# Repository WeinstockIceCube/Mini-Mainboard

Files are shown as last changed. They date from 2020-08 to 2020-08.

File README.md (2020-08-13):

# Mini-Mainboard

This is the public repository for the Altium Project of the Mini-Mainboard for the IceCube calibration devices. 

Further detailed information on the Mini-Mainboard can be found in the DSN on Sharepoint:
https://uwprod.sharepoint.com/:p:/r/sites/icecubeupgrade/_layouts/15/Doc.aspx?sourcedoc=%7Bfcc1f85e-5ff4-41bf-9258-8532a31561ea%7D&action=edit&uid=%7BFCC1F85E-5FF4-41BF-9258-8532A31561EA%7D&ListItemId=355&ListId=%7B73D152DA-70C4-4B92-ADC9-80C59B2FEBA2%7D&odsp=1&env=prod

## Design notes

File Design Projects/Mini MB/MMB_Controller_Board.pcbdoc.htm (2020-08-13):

Reporting Options

# File in Newer Format

Date | : | 12.08.2020
Time | : | 15:29:28
Filename | : | Y:\My Hardware\Altium\IceCube\Mini-Mainboard\MMB_Controller (2-27-2020 2-48-15 PM)\Design Projects\Mini MB\MMB_Controller_Board.pcbdoc

Version | Warning
Release 20.0 | CAUTION - Support of propagation delay for primitives

This file was generated by a later version of the software

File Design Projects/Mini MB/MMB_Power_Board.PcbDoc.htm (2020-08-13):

Reporting Options

# File in Previous Format

Date | : | 13.08.2020
Time | : | 14:24:16
Filename | : | Y:\My Hardware\Altium\IceCube\Mini-Mainboard\MMB_Controller (2-27-2020 2-48-15 PM)\Design Projects\Mini MB\MMB_Power_Board.PcbDoc

Version | Warning

This file was generated by an earlier version of the software

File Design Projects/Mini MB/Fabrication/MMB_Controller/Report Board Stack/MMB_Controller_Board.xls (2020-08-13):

Board Stack Report
Stack Up |  | Layer Stack
Layer | Board Layer Stack | Name | Material | Thickness | Constant
1 |  | Top Paste
2 |  | Top Silk
3 |  | Top Mask | Solder Mask | 0,40mil | 3,5
4 |  | Layer 1 | Copper | 0,70mil
5 |  | Dielectric 1 | 370HR or Equiv | 5,00mil | 4
6 |  | Layer 2P | Copper | 0,70mil
7 |  | Dielectric 2 | 370HR or Equiv | 6,00mil | 4
8 |  | Layer 3 | Copper | 0,71mil
9 |  | Dielectric 3 | 370HR or Equiv | 6,00mil | 4
10 |  | Layer 4 Pow | Copper | 1,38mil
11 |  | Dielectric 4 | 370HR or Equiv | 26,00mil | 4
12 |  | Layer 5 | Copper | 1,38mil
13 |  | Dielectric 5 | 370HR or Equiv | 6,00mil | 4
14 |  | Layer 6 | Copper | 0,71mil
15 |  | Dielectric 6 | 370HR or Equiv | 6,00mil | 4
16 |  | Layer 7P | Copper | 0,70mil
17 |  | Dielectric 7 | 370HR or Equiv | 5,00mil | 4
18 |  | Layer 8 | Copper | 0,70mil
19 |  | Bottom Mask | Solder Mask | 0,40mil | 3,5
20 |  | Bottom Silk
21 |  | Bottom Paste
 | Height : 67,77mil

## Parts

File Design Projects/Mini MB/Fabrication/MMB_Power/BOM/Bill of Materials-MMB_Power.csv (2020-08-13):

Designator | DesignItemId | Quantity | LibRef | Footprint | Manufacturer | Manufacturer Part Number | Supplier 1 | Supplier Part Number 1 | Supplier Stock 1 | Supplier Unit Price 1
C14, C15, C16, C17, C18, C19, C20, C21, C23, C24, C25, C26, C37, C38 | CapC_470nF_1812_450V | 14 | CapC_470nF_1812_450V | 1812 | TDK | CGA8N4X7T2W474M230KE | Digi-Key | 445-7993-1-ND
C22, C29, C39 | CapC_1000pF_1206_1000V | 3 | CapC_1000pF_1206_1000V | CAPC_1206 | KEMET | C1206X102KDRACAUTO | Digi-Key | 399-16729-1-ND
C27, C28 | CAP_FILM_10UF_250V_RAD | 2 | CAP_FILM_10UF_250V_RAD | Cap Radial 1.24" x 0.492" x 0.846 | EPCOS Inc | B32524R3106K | Digi-Key | 495-4799-ND
C30 | CapC_0.1uF_603_50V_GCJ | 1 | CapC_0.1uF_603_50V_GCJ | CAPC_0603 | Murata | GCJ188R71H104KA12D | Digi-Key | 490-5798-1-ND
C31, C32, C33, C34, C35, C36 | CapC_10uF_1206_16V | 6 | CapC_10uF_1206_16V | CAPC_1206 | Murata | GCJ31CR71C106KA15L | Digi-Key | 490-10558-1-ND
D1 | DIODE AVALANCHE 200V 2.0A | 1 | DIODE AVALANCHE 200V 2.0A | DO-214AC | Vishay Semiconductors | BYG22DHE3_A/H | Digi-Key | BYG22DHE3_A/HGICT-ND
L1, L8 | INDUCTOR COM MODE FERR 470.0UH SMD | 2 | INDUCTOR COM MODE FERR 470.0UH SMD | CM6350 | API Delevan Inc | CM6350R-474 | Digi-Key | DN42155-ND
L2, L3, L4, L7, L9, L12 | Ferrite BLM31KN471SH1L | 6 | Ferrite BLM31KN471SH1L | IND_1206 | Murata | BLM31KN471SH1L | Digi-Key | 490-16529-1-ND
L5, L6, L10, L11 | Inductor_330uH_590mA | 4 | Inductor_330uH_590mA | IND_SMD_2P_10.4x10.4x4.8H | TDK EPCOS | B82464G4334M000 | Digi-Key | 495-1804-1-ND
M1 | DC-DC 24 Pin 5Vo | 1 | DC-DC 24 Pin 5Vo | DC_DC_24DIP_9P__V1 | Traco Power | TEN8-7211WI | Digi-Key | 1951-2576-ND
P7 | Header Male SL-5-VERT | 1 | Header Male SL-5-VERT | Header Male 5 Vert | Molex | 70543-0109 | Digi-Key | WM4125-ND
PAB | 61201020621 | 1 | 61201020621 | 61201020621
PTP1 | Test Point SM | 1 | Test Point SM | Test Point SM | Keystone Electronics | 5019 | Digi-Key | 5019KCT-ND
PX3 | Harwin 4x1 2mm | 1 | Harwin 4x1 2mm | HARWIN M80-8820442 | Harwin | M80-8820442 | Digi-Key | 952-1071-5-ND
PX4 | Harwin 5x1 2mm | 1 | Harwin 5x1 2mm | HARWIN M80-8820542 | Harwin | M80-8820542 | Digi-Key | 952-1072-5-ND
R17, R18, R19, R20 | R_4.7M_1206_1% | 4 | R_4.7M_1206_1% | RES_1206 | Rohm | KTR18EZPF4704 | Digi-Key | RHM4.7MAICT-ND
RX10 | R_ZERO_805 | 1 | R_ZERO_805 | RES_0805 | Panasonic | ERJ6GEY0R00V | Digi-Key | P0.0ACT-ND
SC1, SC2 | Spring Contact | 2 | Spring Contact | Spring Contact SM | Harwin | S1941-42R | Digi-Key | 952-3245-1-ND
WT1, WT2, WT3, WT4, WT5, WT6, WT7 | Test Point Turret | 7 | Test Point Turret | Turret-1592 | Mill-Max | 2506-3-00-80-00-00-07-0 | Digi-Key | ED11398-ND

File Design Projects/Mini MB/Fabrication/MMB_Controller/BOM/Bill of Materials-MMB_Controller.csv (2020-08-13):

Designator | DesignItemId | Quantity | Footprint | Manufacturer | Manufacturer Part Number | Supplier 1 | Supplier Part Number 1
C1, C2, C3, C4, C40, C43, C45, C46, C47, C50, C55, C56, C57, C58, C59, C60, C61, C62, C63, C64, C65, C66, C67, C96, C98, C100, C102, C104, C105, C106, C108, C131, C132 | CapC_0.1uF_603_50V | 33 | CAPC_0603 | TDK | CGJ3E2X7R1H104K080AA | Digi-Key | 445-8122-1-ND
C5, C8, C11, C51, C54, C68, C70, C72, C73, C74, C75, C77, C79, C80, C81, C82, C84, C86, C87, C88, C89, C91, C93, C94, C95, C110, C115, C119, C123, C133, C134 | CapC_10uF_805_10V | 31 | CAPC_0805 | Murata | GCJ21BR71A106KE01L | Digi-Key | 490-12646-1-ND
C6, C7, C9, C10, C12, C13, C41, C49, C69, C71, C76, C78, C83, C85, C90, C92, C116, C117, C118, C120, C121, C122, C124, C125, C126 | CapC_0.1uF_603_50V_GCJ | 25 | CAPC_0603 | Murata | GCJ188R71H104KA12D | Digi-Key | 490-5798-1-ND
C42 | CapC_10uF_1206_16V | 1 | CAPC_1206 | Murata | GCJ31CR71C106KA15L | Digi-Key | 490-10558-1-ND
C44, C48 | CMP-2000-06338-1 | 2 | CAPC1608X90X35LL10T15 | Murata
C52, C53 | CapC_2.2uF_805_16V | 2 | CAPC_0805 | Murata | GCJ21BR71C225KA13L | Digi-Key | 490-5801-1-ND
C97, C99, C101, C103, C107, C109, C111, C114, C127, C129 | CapC_1.0uF_603_25V | 10 | CAPC_0603 | Murata | GCJ188R71E105KA01D | Digi-Key | 490-14409-1-ND
C112, C113, C128, C130 | CapC_1000pF_603_50V | 4 | CAPC_0603 | Knowles Syfer | 0603Y0500102KXT | Digi-Key | 1608-1367-1-ND
D2, D3 | Diode ESD Pair | 2 | SOT-23 | ON Semiconductor | SBAT54SLT1G | Digi-Key | SBAT54SLT1GOSCT-ND
ICM1 | Ice Comms Module | 1 | Ice Comms Module
ICM-J1, ICM-J2 | SFM-115-X2-XXX-D-A | 2 | SFM-115-X2-XXX-D-A | Samtec | SFM-115-02-S-D-A-K-TR | Digi-Key | SAM13245CT-ND
ICM-MH1, ICM-MH2 | Keystone 4883 | 2 | Keystone 4883 solder | Keystone Electronics | 4883 | Digi-Key | 36-4883CT-ND
J2, J3 | SMA-Vertical | 2 | SMA Vertical 200LS | Emerson Network Power Connectivity Johnson | 142-0701-231 | Digi-Key | J608-ND
L13, L14, L15, L16, L17, L18, L19, L20, L21, L22, L23, L24 | Bead SM_805_4.0A_TDK | 12 | SMD-0805 | TDK | MPZ2012S101ATD25 | Digi-Key | 445-172903-1-ND
L27, L28 | Bead SM_805_2.5A_TDK | 2 | SMD-0805 | TDK | MPZ2012S331ATD25 | Digi-Key | 445-172907-1-ND
P1, P13, P14 | 62100821021 | 3 | 62100821021
P2, P6 | 62101021021 | 2 | 62101021021
P9 | Header Male SL-6-VERT | 1 | Header Male 6 Vert | Molex | 0705430110 | Digi-Key | WM4126-ND
P10 | 61000618221 | 1 | 61000618221
P11, P12, P15 | Header Male 3M-452 15x2 | 3 | 45230-220230 | 3M | 45230-220230 | Digi-Key | 3M15579CT-ND
P16, P17 | 62100421021 | 2 | 62100421021
P33 | 62130621021 | 1 | 62130621021
PBA | 61201020621 | 1 | 61201020621
R1, R3, R4, R6 | R_243_603_1% | 4 | RES_0603 | Panasonic | ERJ3EKF2430V | Digi-Key | P243HCT-ND
R2, R5, R7, R8 | R_4.99K_603_1% | 4 | RES_0603 | Panasonic | ERJ3EKF4991V | Digi-Key | P4.99KHCT-ND
R11, R12, R13, R14, R15, R16, R25, R26, R40, R41, R42, R44, R45, R46, R47, R48, R49, R50, R51, R52, R53, R54, R55, R56, R57, R58, R59, R60, R61, R62, R63, R64, R65, R66, R67, R68, R69, R70, R71, R72 | R_28.0_603_1% | 40 | RES_0603 | Panasonic | ERJ3EKF28R0V | Digi-Key | P28.0HCT-ND
R21, R22, R23, R24 | R_3.00K_603_1% | 4 | RES_0603 | Panasonic | ERJ3EKF3001V | Digi-Key | P3.00KHCT-ND
R27, R28, R29, R30 | R_100K_603_1% | 4 | RES_0603 | Panasonic | ERJ3EKF1003V | Digi-Key | P100KHTR-ND
R31 | R_10.0K_603_1% | 1 | RES_0603 | Panasonic | ERJ3EKF1002V | Digi-Key | P10.0KHCT-ND
R33, R34, R35, R36 | R_39.2_603_1% | 4 | RES_0603 | Panasonic | ERJ-3EKF39R2V | Digi-Key | P39.2HCT-ND
R37, R38, R301, R302 | R_2.00K_603_1% | 4 | RES_0603 | Panasonic | ERJ3EKF2001V | Digi-Key | P2.00KHCT-ND
R39, R43 | R_49.9_1206_1% | 2 | RES_1206 | Panasonic | ERJ8ENF49R9V | Digi-Key | P49.9FCT-ND
R73, R74, R75, R76, R77, R78, R79, R80 | R_49.9_603_1% | 8 | RES_0603 | Panasonic | ERJ3EKF49R9V | Digi-Key | P49.9HCT-ND
TP1, TP2, TP3, TP4, TP5 | Test Point SM | 5 | Test Point SM | Keystone Electronics | 5019 | Digi-Key | 5019KCT-ND
U1, U2, U7, U17 | SN74LVC2T45QDCURQ1 | 4 | TI-DGK8_N | Texas Instruments | SN74LVC2T45MDCTTEP | Digi-Key | 296-23952-1-ND
U3 | DS24B33S+T&R | 1 | W8+2_M | Maxim | DS24B33S+T&R | Digi-Key | DS24B33S+T&RCT-ND
U4 | S25FS512SAGMFV010 | 1 | MICT-SF-16_N | Cypress | S25FS512SAGMFV010 | Digi-Key | S25FS512SAGMFV010-ND
U5 | STM32H743ZIT6 | 1 | STM-LQFP144_N | STMicroelectronics | STM32H743ZIT6 | Digi-Key | 497-17721-ND
U6, U9, U13, U15, U16 | DS90LV012ATMF | 5 | MF05A_N | TI National Semiconductor | DS90LV012ATMF/NOPB | Digi-Key | DS90LV012ATMF/NOPBCT-ND
U8 | NUP4301MR6T1G | 1 | ONSC-SC-74-6-318F-05_V | ON Semiconductor | NUP4301MR6T1G | Digi-Key | NUP4301MR6T1GOSCT-ND
U10 | LPS22HDTR | 1 | HLGA-10L | STMicroelectronics | LPS22HDTR | Digi-Key | 497-17587-1-ND
U11 | LIS3MDLTR | 1 | VFLGA-12 | STMicroelectronics | LIS3MDLTR | Digi-Key | 497-13892-1-ND
U12 | ADXL355BEZ-RL7 | 1 | E-14-1 | Analog Devices | ADXL355BEZ-RL7 | Digi-Key | ADXL355BEZ-RL7CT-ND
U14 | DS90LV011ATMF | 1 | MF05A_N | Texas Instruments | DS90LV011ATMF/NOPB | Digi-Key | DS90LV011ATMF/NOPBCT-ND

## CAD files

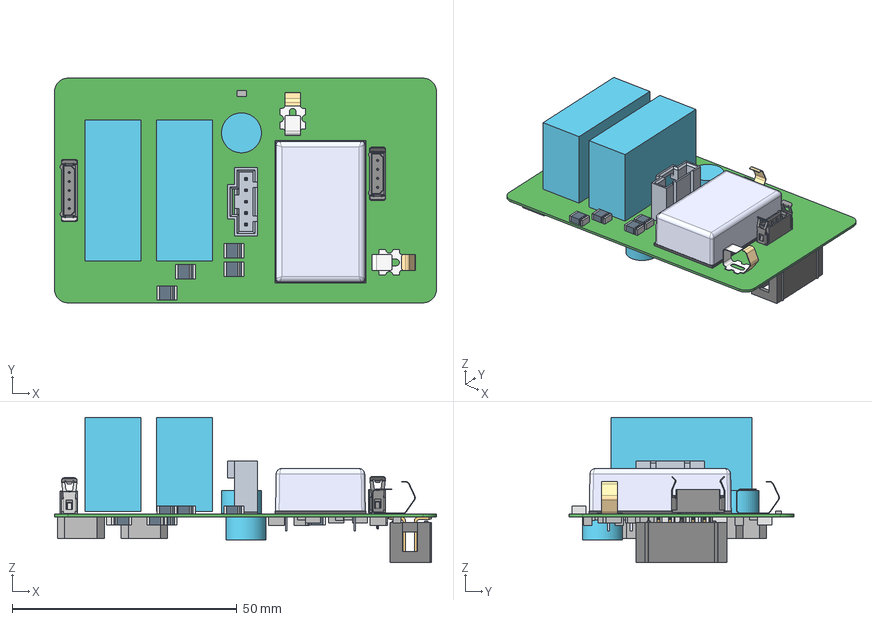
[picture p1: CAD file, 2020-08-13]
Design Projects/Mini MB/ReviewDocs/ExportSTEP/MMB_Power_Board.step
85.0 x 50.0 x 32.3 mm
s1941-42 x 2
Extruded x 99
6120xx20621_PIN x 10
M80-1000598
M80-0200049 x 9
M80-001XXXX x 4
M80-1000498
ten8wi

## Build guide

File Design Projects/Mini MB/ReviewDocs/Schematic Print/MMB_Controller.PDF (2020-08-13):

D | D
C | C
B | B
A | A

## Revisions.SchDoc

13.05.2020 | 15:40:26
Y:\My Hardware\Altium\IceCube\Mini-Mainboard\MMB_Controller (2-27-2020 2-48-15 PM)\Design Projects\Mini MB\Revisions.SchDoc
Size: | Designed:

Modified:
File:

Revision:

Time: | Sheet | of
B | Drafted: | PWS PWS
| Checked:

Started:

Approve:

# IceCube Upgrade Mini MB Schematic Revision History:

Rev1 Jan 28 2019 | Rev1.0 Prototype run of (x) PCB Assemblies SN1-SNx

# Mini MB Production History

Older Revision Perry
1. Transferred selected design files from PDOM project
2. MCU: Removed Net OSC_MCU_CLOCK from MCU Pin 8 = PC14-OSC32_IN.
3. MCU: Added Test point to OSC_MCU_OUT.
4. ICM: Added ICM_+1V8 net to J1-12. (fixed initial error with connection to J1-8)
5. ICM, XTIO: Changed LVDS signals ICM_CAL_TRIG and ICM_CAL_TIME from 3.3V psuedo-diff to 1.8V Diff SSTL 1 (0.9Vcm).
6. ALL: Re-annotated all sheets.
7. MCU: Removed redundant write-protect bypass jumper.
8. XTIO: Added SMA TRIG OUT and SMA TIME IN connectors, Diff-SE converters and jumper selects.
9. ICM: Added bypass caps on ICM Power in and out
10. MCU: Added connector for Ethernet PHY
11. MCU Changed Ethernet Connector to 2x8 x 0.1"
12. XTIO: Added jumpers for optional termination of LVDS lines
13. XTIO: Fixed net going to Pin2 of P18 to be "ICM_FPGA_CLOCK_N" (was _P)
14. MCU: Changed connector for Ethernet PHY Card to type: SFM-115-X2-XXX-D-A
15. PHY: Removed, LVS1: Removed J1, ICM: Removed USB1 and ICM-JTAG Feldhäuser:
16. ICM: P1 changed to smaller type
17. ICM: Connect Mini MB B to Mini MB A with PBA, PAB for cable connection
18. ICM: P2 changed to smaller type
19. ICM: P6 changed to smaller type
20. ICM: Connection ICM_FPGA_GPIO_0 to GND cut (R11)
21. ICM: Penetrator from ICM to LVS1 on Mini MB A
22. MCU: P10 changed to smaller type
23 XTIO P13,. P14, P16, P17 changed to smaller type
24. Delete following (only one pin, Electr. Rule Check)
: +5V0_EXT P2-4, ICM_TCK ICM-J1-18, ICM_TDI ICM-J1-14, ICM_TDO ICM-J1-16, ICM_TMS ICM-J1-20 MCU_INTLK U5-46, Aux_P3V3_EN U5-112,
MCU_CAL_A3 U5-47, MCU_GPIO_0 U5-98, MCU_GPIO_01 U5-99, MCU_GPIO_2 U5-113, NetP9_6 P9-6, NetU8_1 U8-1, NetU8_3 U8-3,
NetU12_12 U12-12, NetU12_13 U12-13, NetU12_14 U12-14
25. Delete Floating Net Label MCU_GPIO_3
26. Layer changed in PCB

# Download .pdf for component details Click on schematic symbols for component data

Temprary list made by Perry on 2-27/2-28
MCU: Added Jumpers ID0-ID3 see "DOM_Type_ID_Jumpers" in shared docs LVS1: Layout note: keep PX3 and PX4 close to each other (from same cable) LVS1: Added (2) spring contacts for grounding DC-DC converter case.
SLO: Removed L25, L26,L27,L29 Added 2x10uF bypass on magnetormeter U11 ICM: Probably need some ICM JTAG connection?
SLO: Replaced Pressure sensor with different part# for better availability

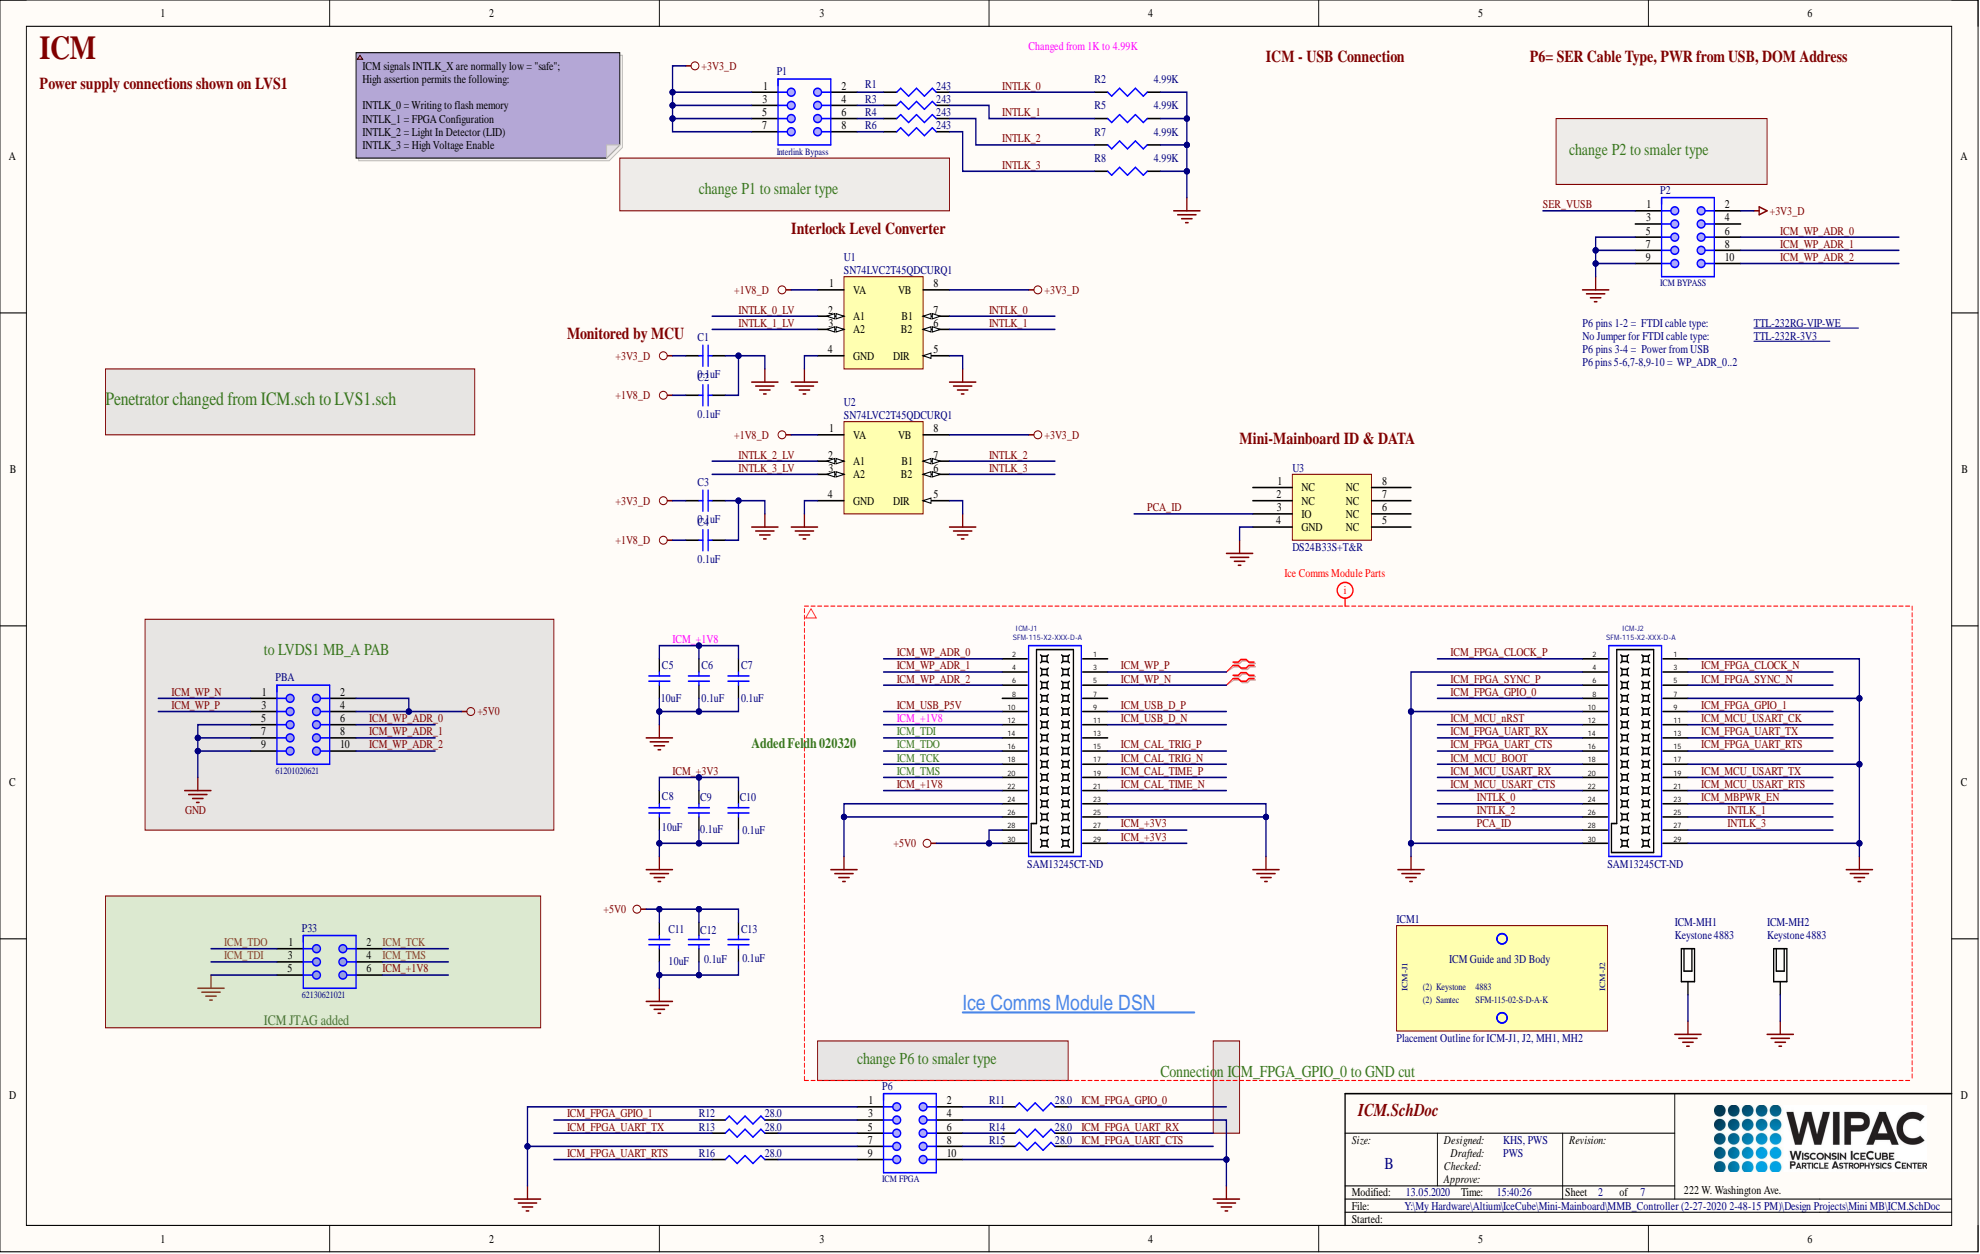
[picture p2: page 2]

ICM signals INTLK_X are normally low = "safe";
High assertion permits the following:

Power supply connections shown on LVS1

INTLK_0 = Writing to flash memory
INTLK_1 = FPGA Configuration
INTLK_2 = Light In Detector (LID)
INTLK_3 = High Voltage Enable

change P2 to smaler type

change P1 to smaler type

Penetrator changed from ICM.sch to LVS1.sch

Mini-Mainboard ID & DATA

Ice Comms Module Parts

ICM Guide and 3D Body

Ice Comms Module DSN

Placement Outline for ICM-J1, J2, MH1, MH2

Connection ICM_FPGA_GPIO_0 to GND cut change P6 to smaler type

Y:\My Hardware\Altium\IceCube\Mini-Mainboard\MMB_Controller (2-27-2020 2-48-15 PM)\Design Projects\Mini MB\ICM.SchDoc

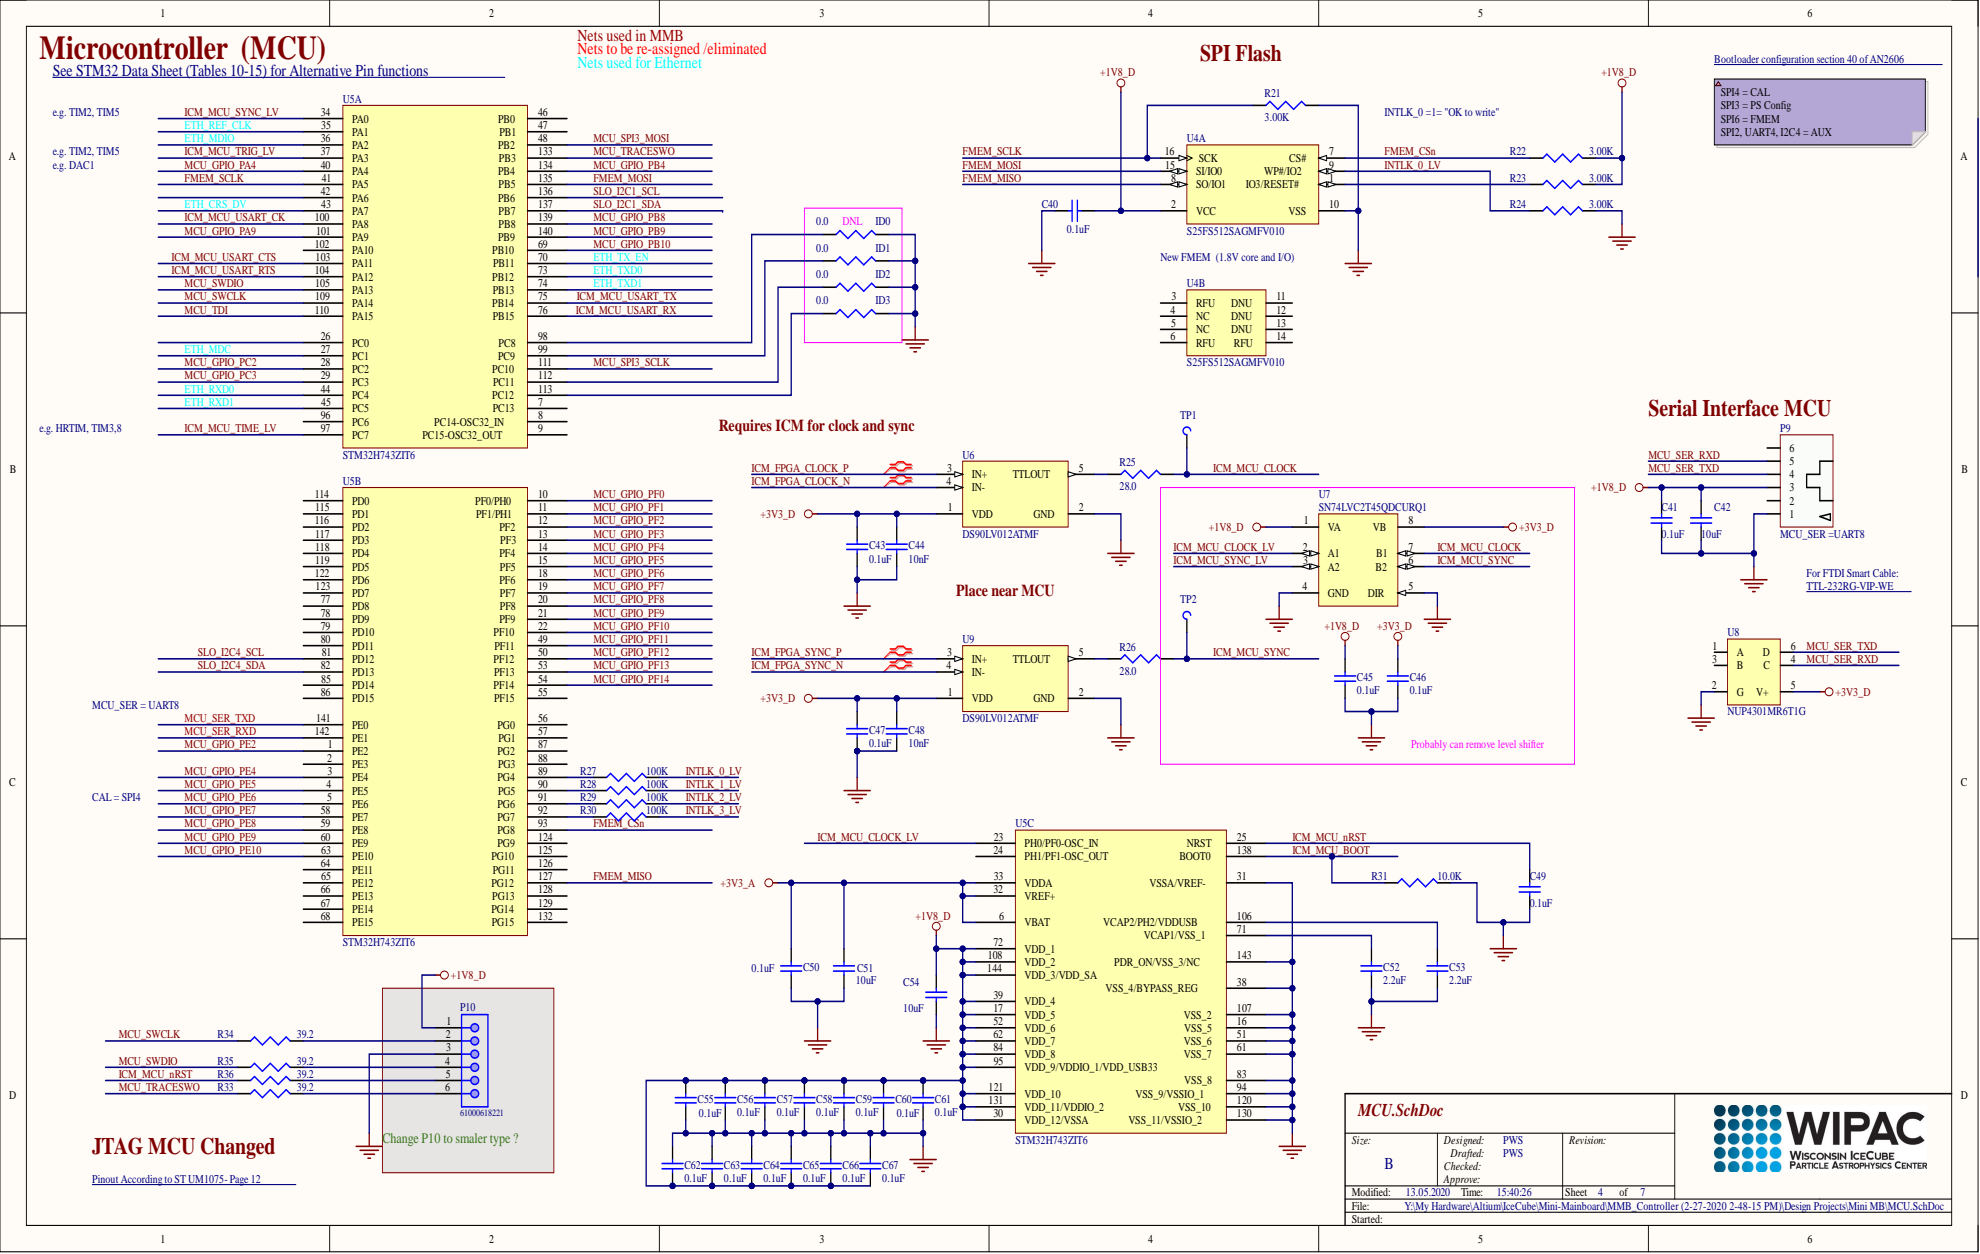
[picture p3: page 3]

9 9
1 1 1 | MCU _SPI 3 _SCL K

1 0 8
1 4 4 | | 3 8

1 7
5 2 | 1 6
6 2 | 5 1
8 4 | 6 1
9 5 | 8 3

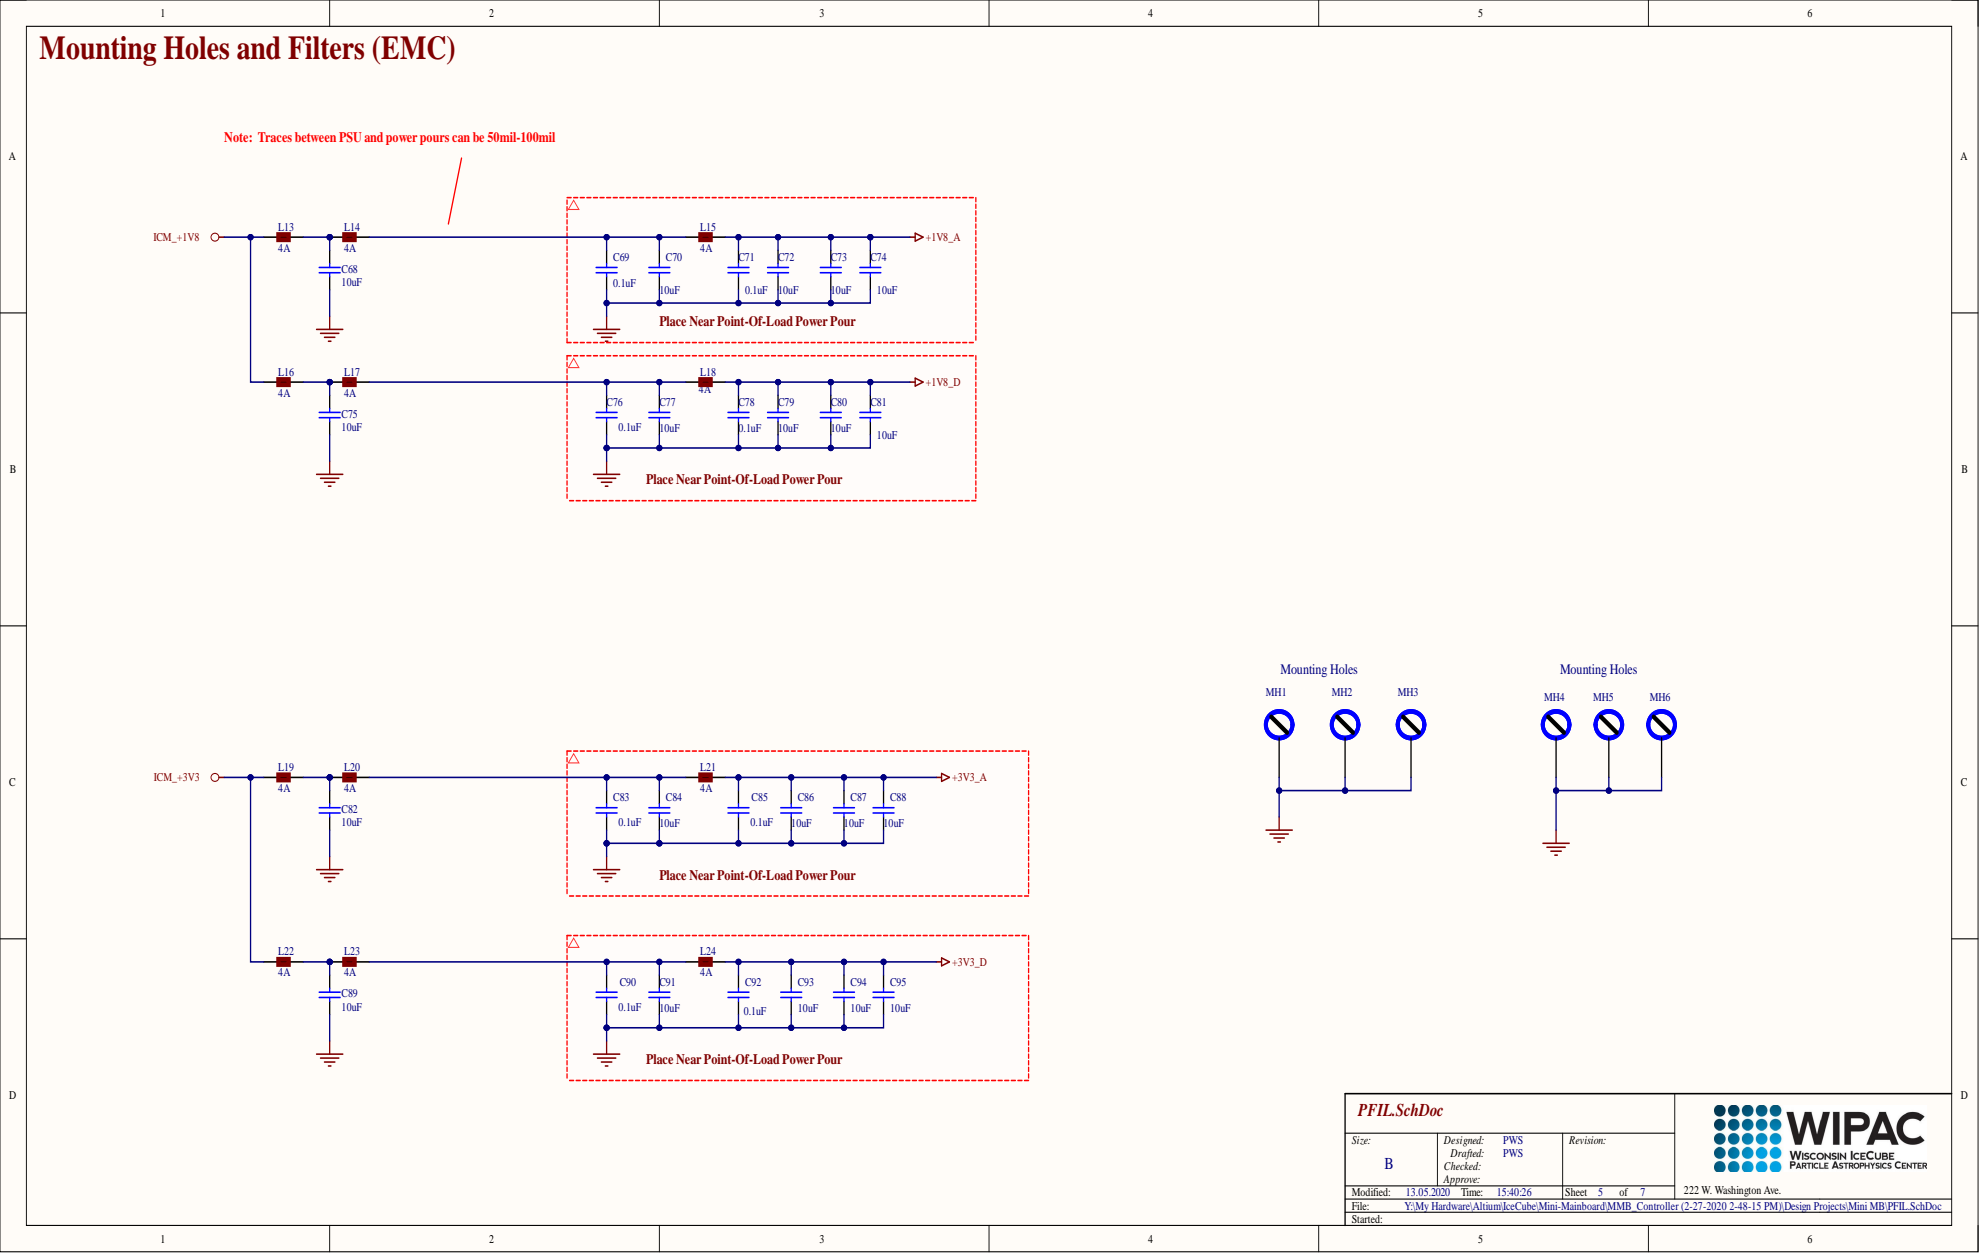
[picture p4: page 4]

Mounting Holes and Filters (EMC)

Note: Traces between PSU and power pours can be 50mil-100mil

Place Near Point-Of-Load Power Pour

Y:\My Hardware\Altium\IceCube\Mini-Mainboard\MMB_Controller (2-27-2020 2-48-15 PM)\Design Projects\Mini MB\PFIL.SchDoc

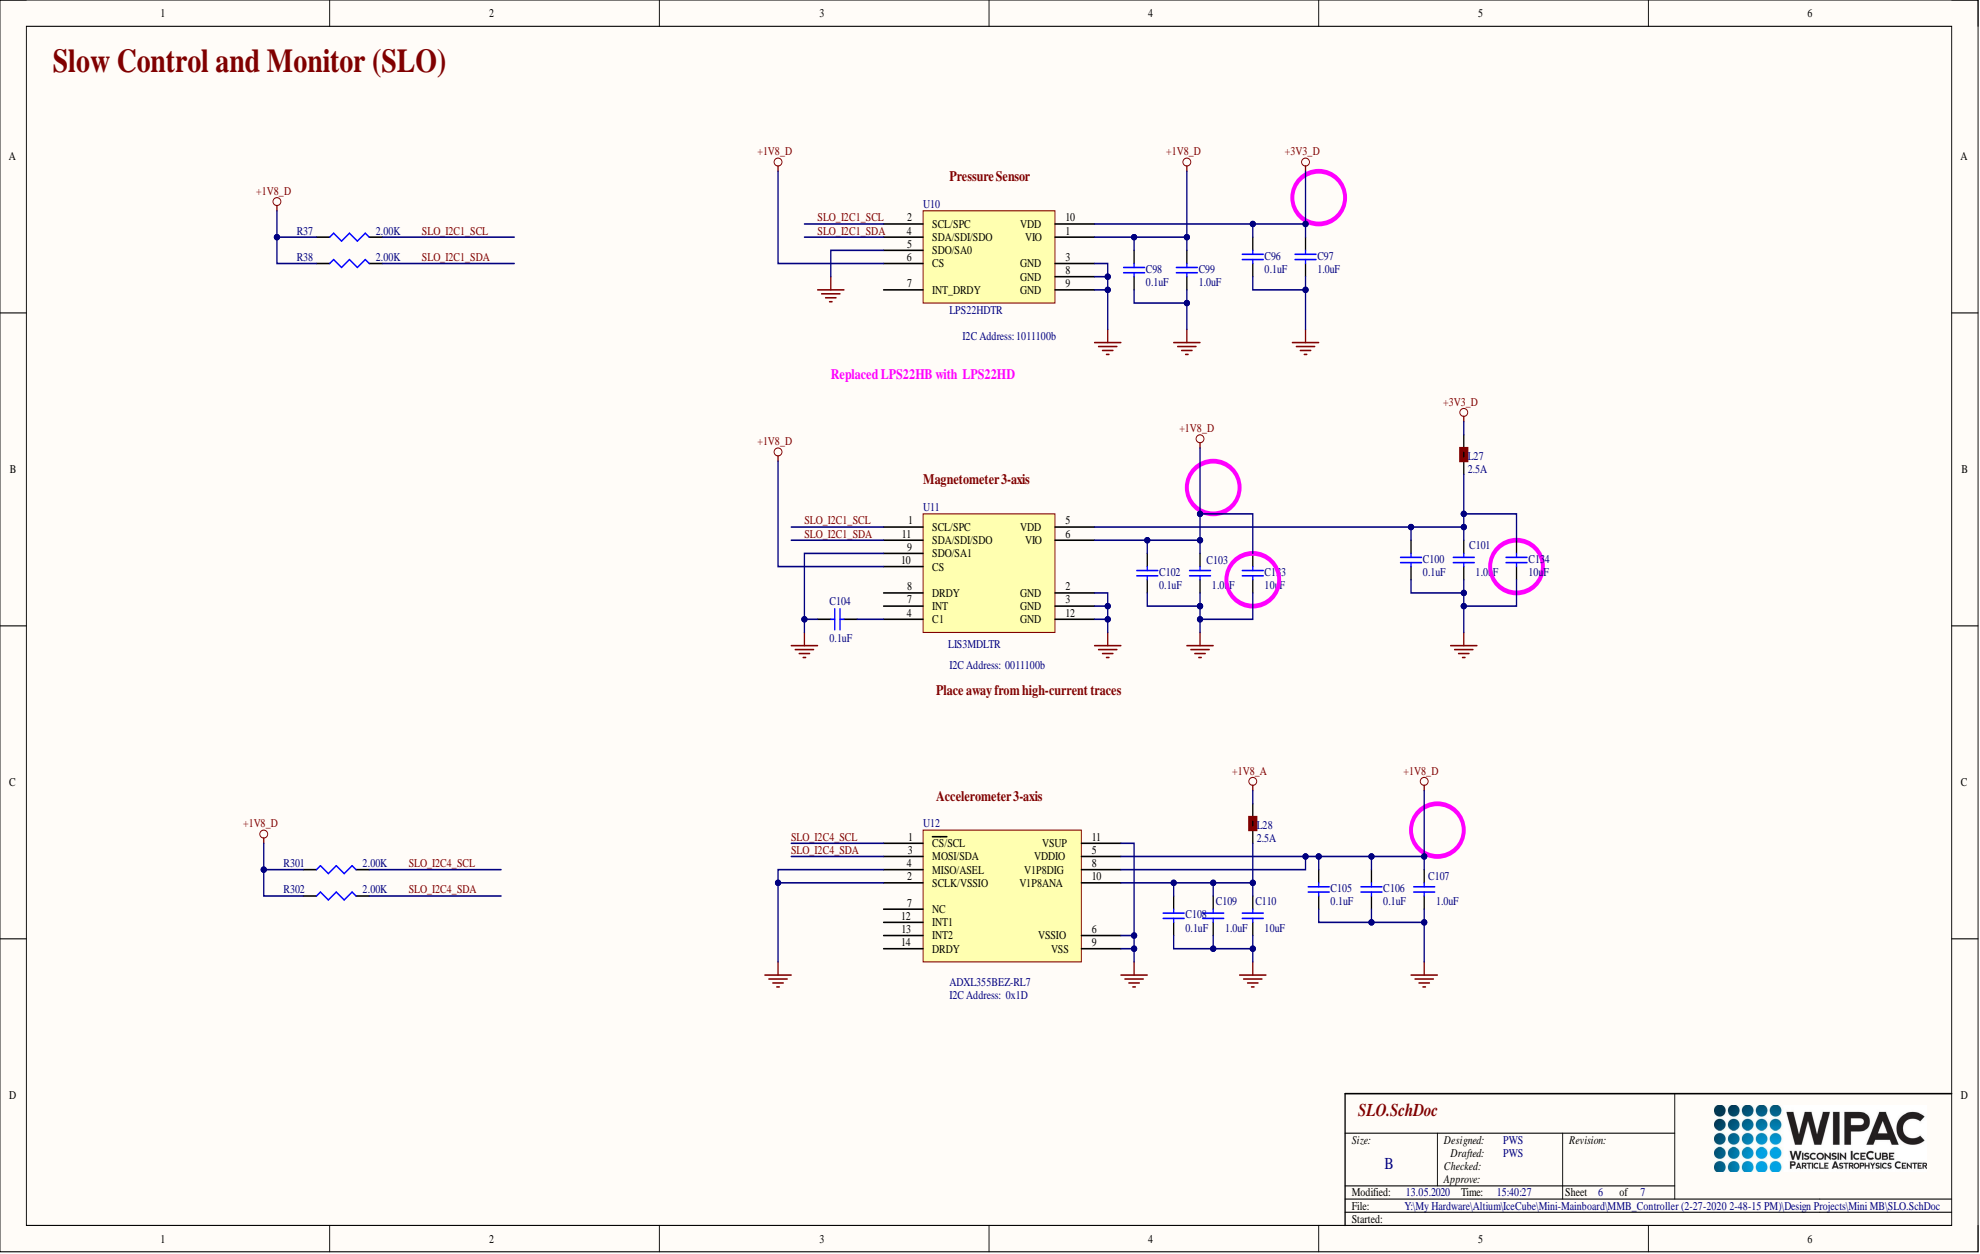
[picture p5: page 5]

Slow Control and Monitor (SLO)

I2C Address: 0011100b
Place away from high-current traces

Y:\My Hardware\Altium\IceCube\Mini-Mainboard\MMB_Controller (2-27-2020 2-48-15 PM)\Design Projects\Mini MB\SLO.SchDoc

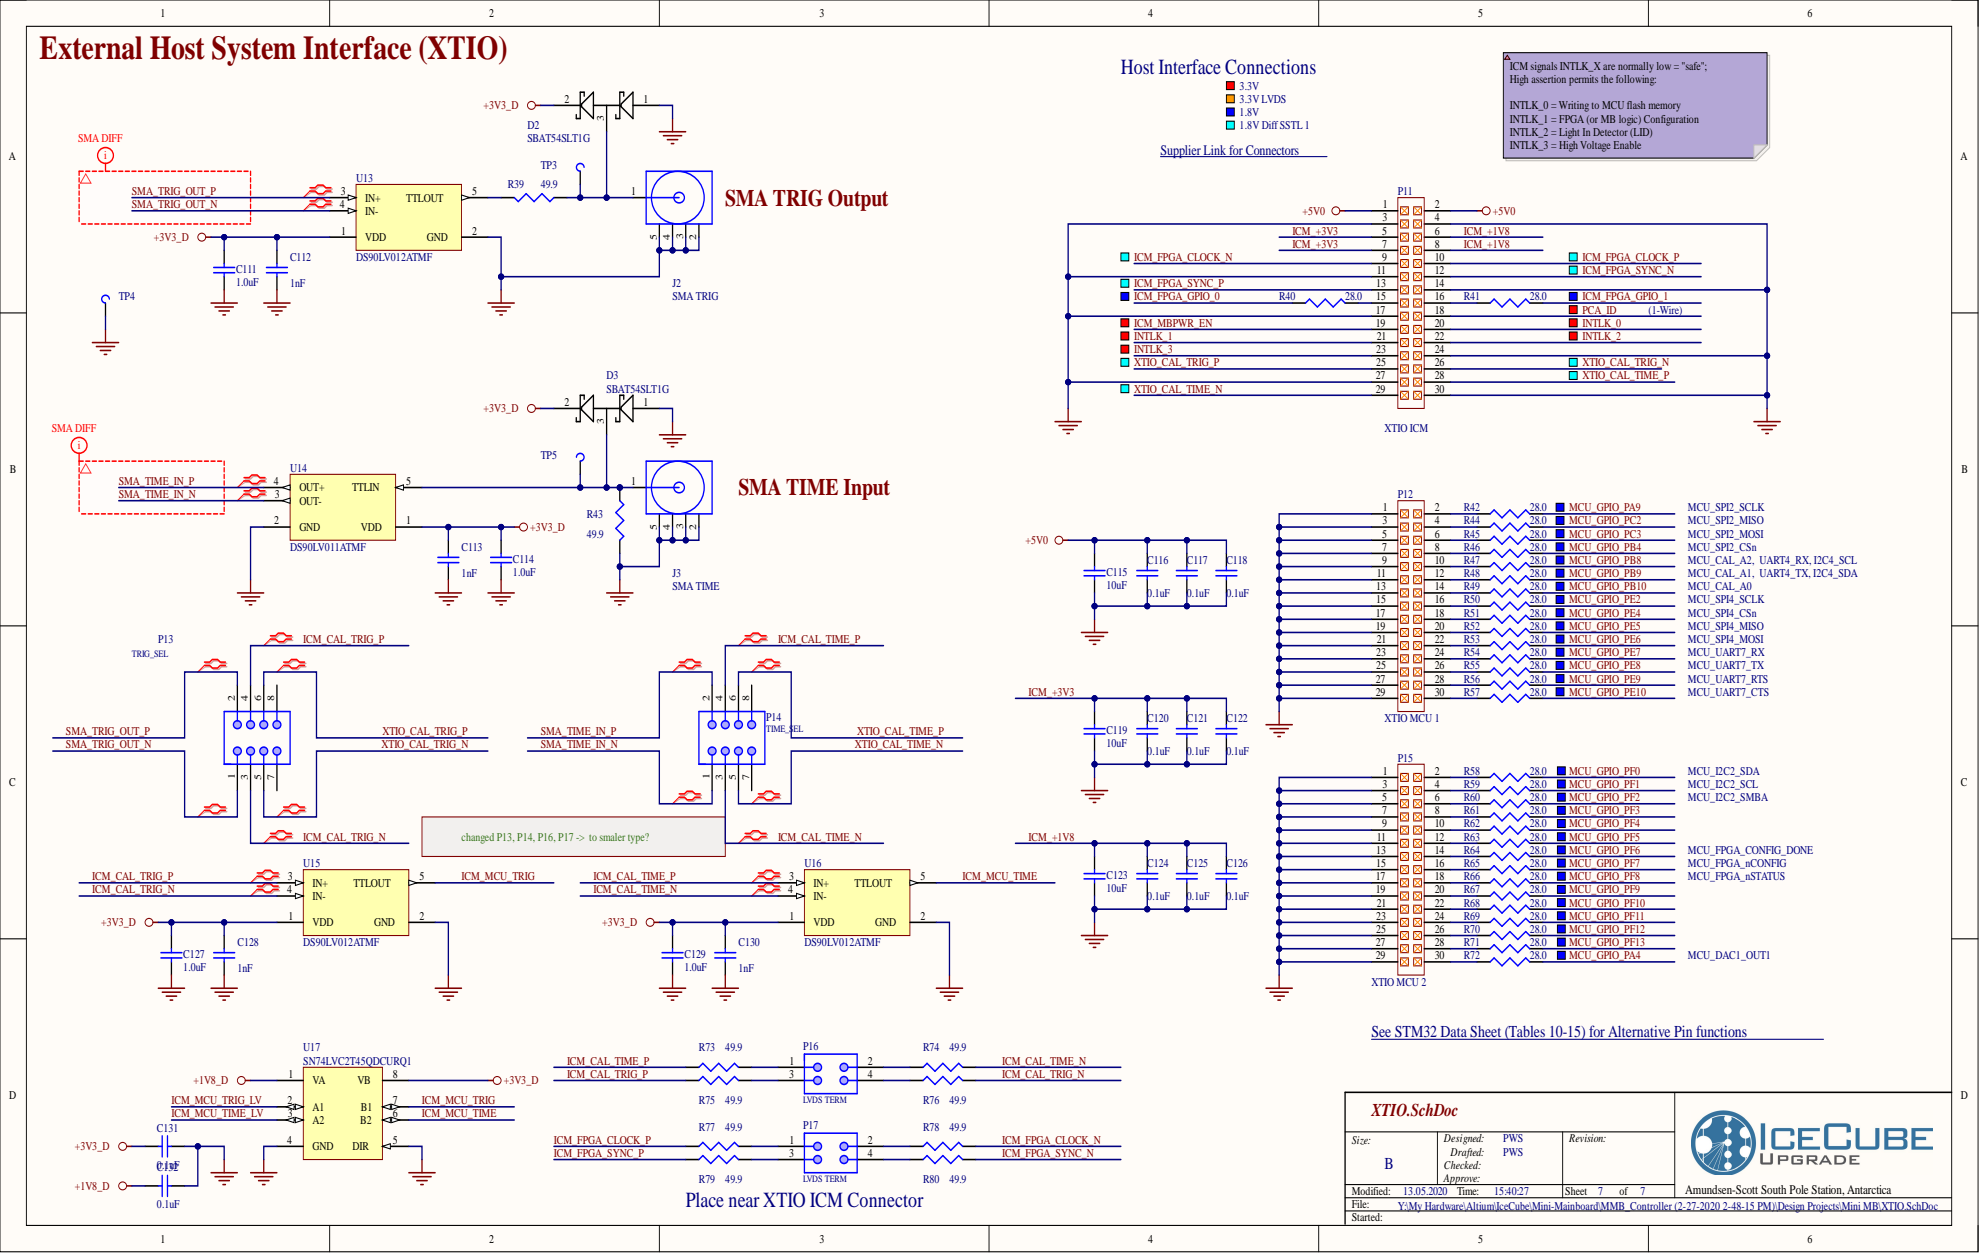
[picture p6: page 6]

External Host System Interface (XTIO)

ICM signals INTLK_X are normally low = "safe";
High assertion permits the following:

INTLK_0 = Writing to MCU flash memory
INTLK_1 = FPGA (or MB logic) Configuration
INTLK_2 = Light In Detector (LID)
INTLK_3 = High Voltage Enable

Supplier Link for Connectors (https://www.digikey.com/products/en?keywords=3M15579CT-ND)

changed P13, P14, P16, P17 -> to smaler type?

See STM32 Data Sheet (Tables 10-15) for Alternative Pin functions (https://www.st.com/resource/en/datasheet/stm32h743bi.pdf)

Place near XTIO ICM Connector +1V8_D

Y:\My Hardware\Altium\IceCube\Mini-Mainboard\MMB_Controller (2-27-2020 2-48-15 PM)\Design Projects\Mini MB\XTIO.SchDoc

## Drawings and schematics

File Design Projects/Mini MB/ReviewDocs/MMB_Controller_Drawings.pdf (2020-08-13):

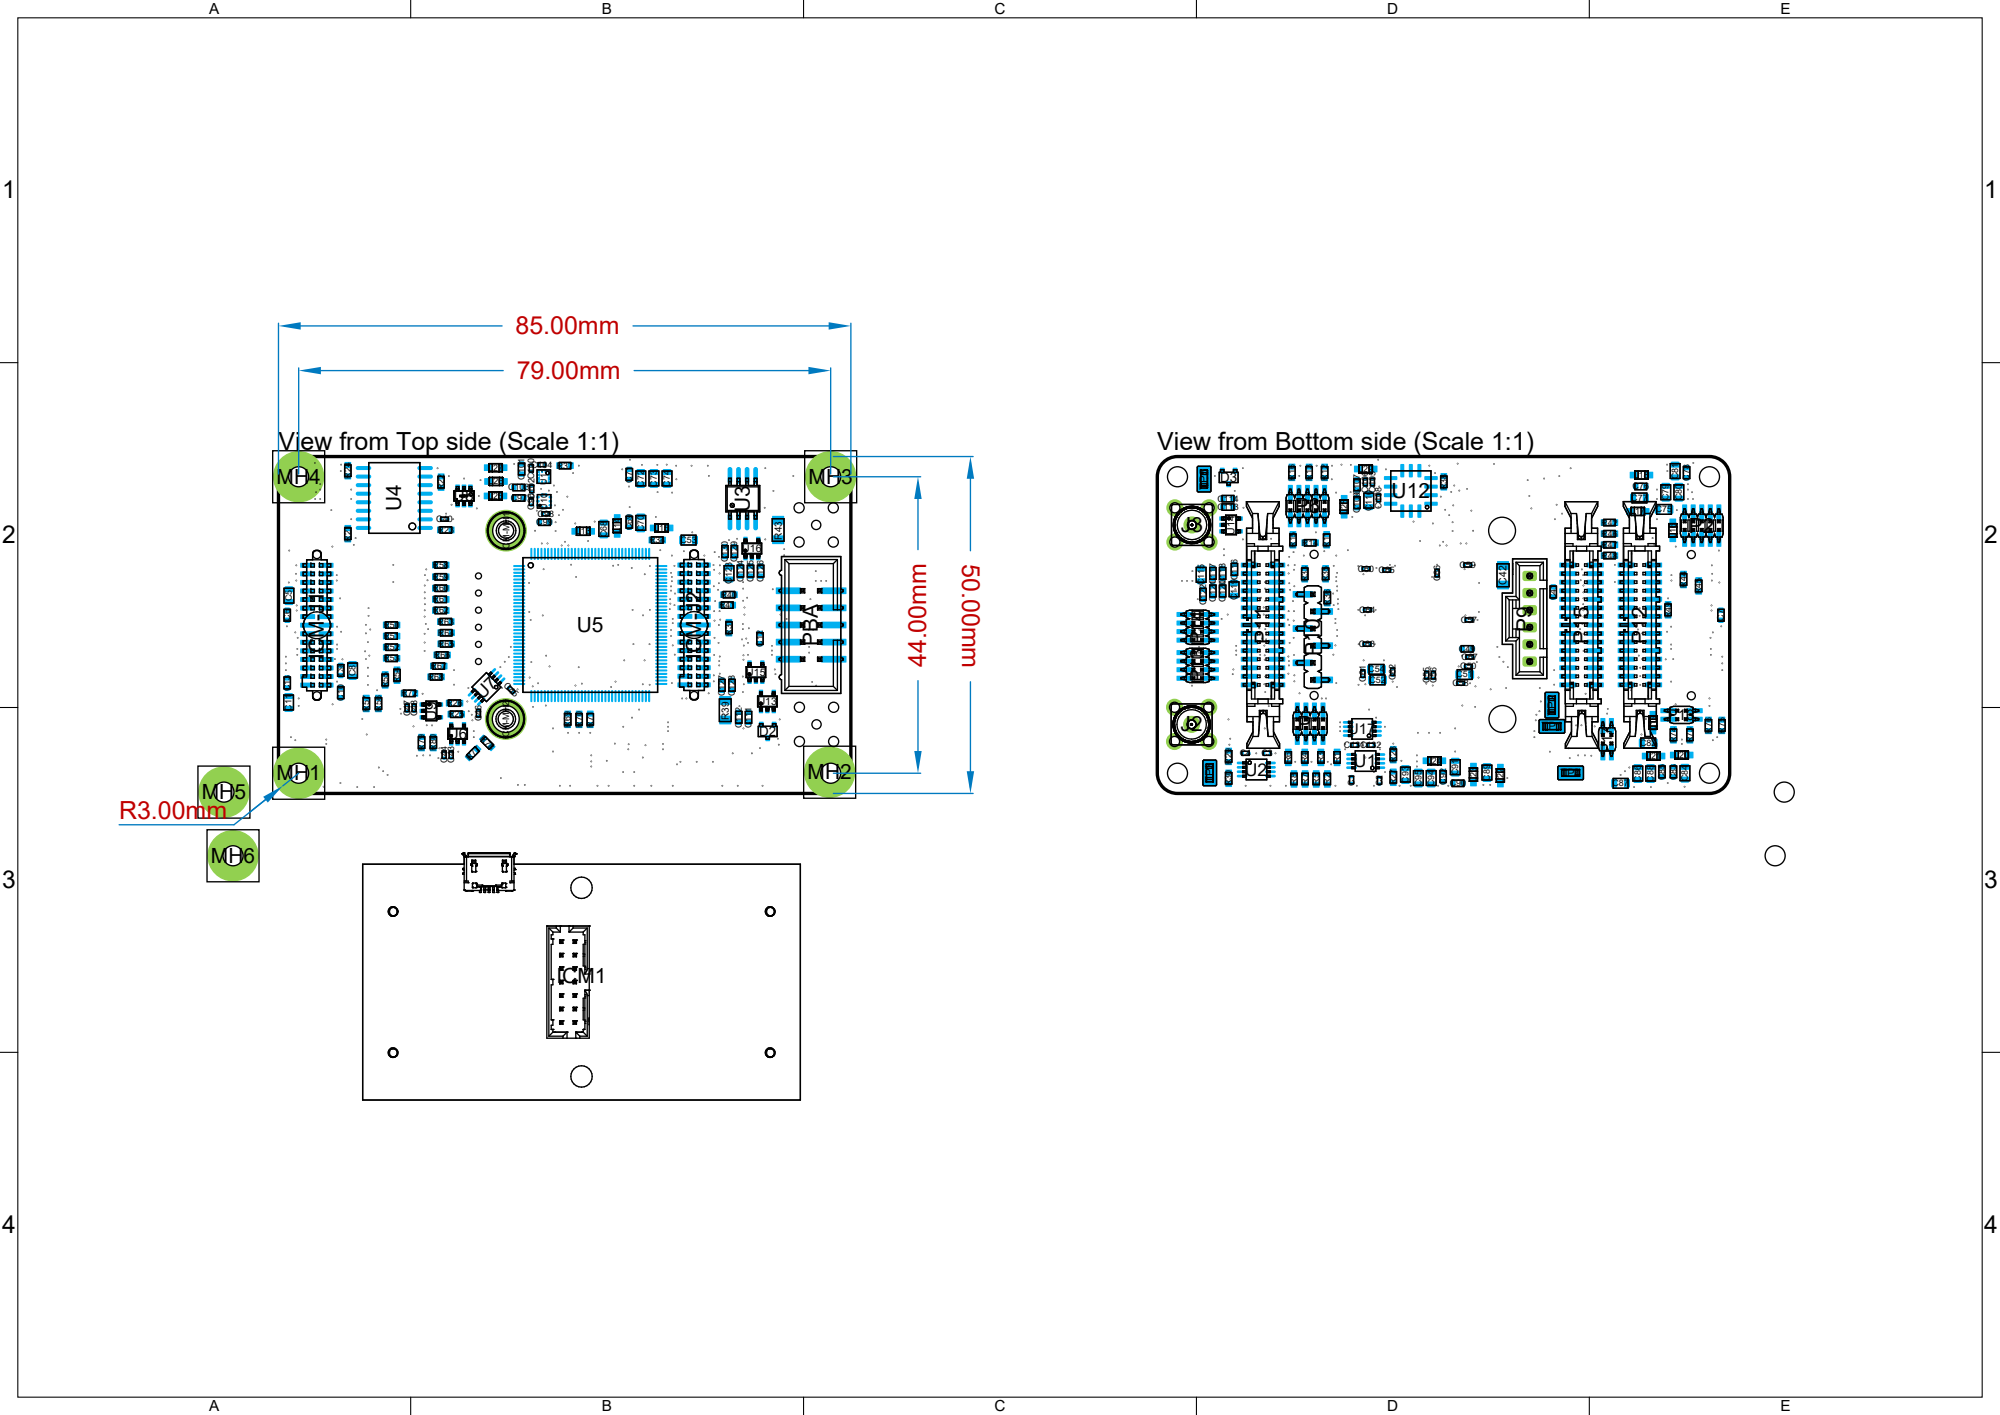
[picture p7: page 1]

View from Top side (Scale 1:1)

View from Bottom side (Scale 1:1)

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
1 | 1
2 | 2
3 | 3
4 | 4
Material | Layer | Thickness Dielectric Material Type | Gerber
| Top Silk | | Legend | GTO
Surface Material Top Mask | 0.01mm | Solder Mask | Solder Mask GTS
Copper | Layer 1 | 0.02mm | Signal | GTL
Core | 0.13mm | 370HR or Equiv | Dielectric
Copper | Layer 2P | 0.02mm | Internal Plane GP1
Prepreg | 0.15mm | 370HR or Equiv | Dielectric
CF-003 | Layer 3 | 0.02mm | Signal | G1
Core | 0.15mm | 370HR or Equiv | Dielectric
CF-004 | Layer 4 Pow | 0.04mm | Signal | G2
Prepreg | 0.66mm | 370HR or Equiv | Dielectric
CF-004 | Layer 5 | 0.04mm | Signal | G3
Core | 0.15mm | 370HR or Equiv | Dielectric
CF-003 | Layer 6 | 0.02mm | Signal | G4
Prepreg | 0.15mm | 370HR or Equiv | Dielectric
Copper | Layer 7P | 0.02mm | Internal Plane GP2
Core | 0.13mm | 370HR or Equiv | Dielectric
Copper | Layer 8 | 0.02mm | Signal | GBL
Surface Material Bottom Mask 0.01mm | Solder Mask | Solder Mask GBS
| Bottom Silk | | Legend | GBO
Total thickness: 1.72mm

Layer Stack Legend

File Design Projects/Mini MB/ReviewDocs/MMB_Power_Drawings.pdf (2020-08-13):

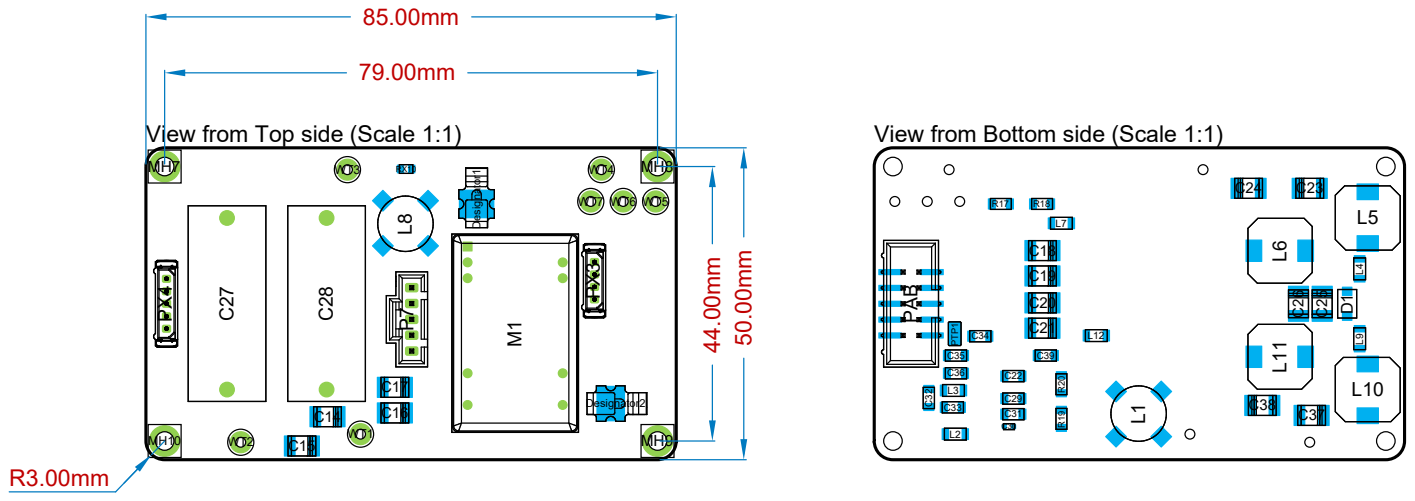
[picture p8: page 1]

View from Top side (Scale 1:1)

View from Bottom side (Scale 1:1)

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
1 | 1
2 | 2
3 | 3
4 | 4
Material | Layer | Thickness Dielectric Material Type | Gerber
| Top Overlay | | Legend | GTO
Surface Material Top Solder | 0.01mm | Solder Resist | Solder Mask GTS
Copper | Top Layer | 0.04mm | Signal | GTL
Prepreg | 0.07mm | PP-006 | Dielectric
CF-004 | Layer 1 | 0.04mm | Internal Plane GP1
0.32mm | FR-4 | Dielectric
CF-004 | Layer 2 | 0.04mm | Internal Plane GP2
Prepreg | 0.07mm | PP-006 | Dielectric
Copper | Bottom Layer | 0.04mm | Signal | GBL
Surface Material Bottom Solder 0.01mm | Solder Resist | Solder Mask GBS
| Bottom Overlay | | Legend | GBO
Total thickness: 0.62mm

Layer Stack Legend

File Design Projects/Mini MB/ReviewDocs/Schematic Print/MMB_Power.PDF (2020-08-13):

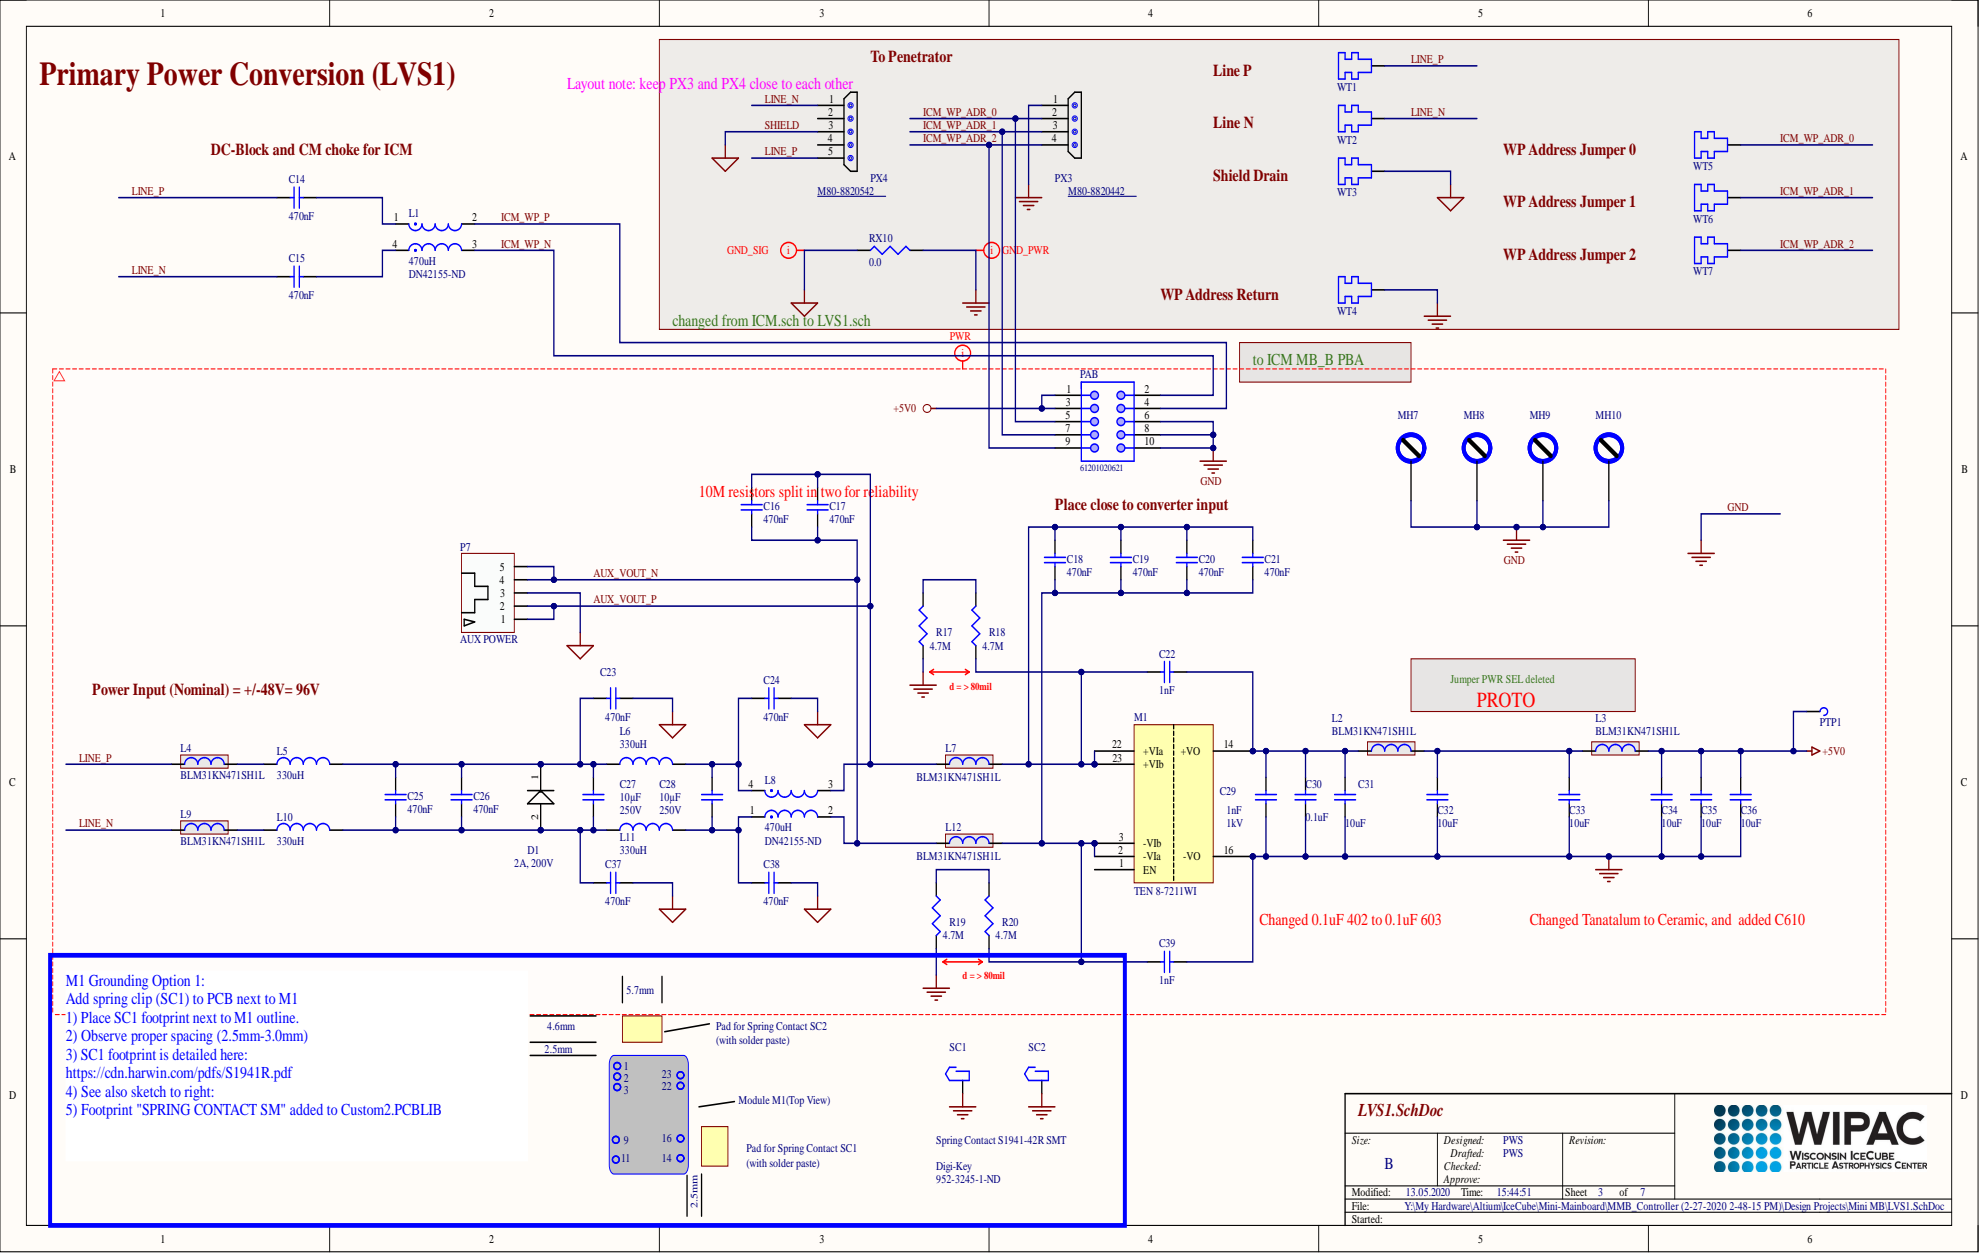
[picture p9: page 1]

Layout note: keep PX3 and PX4 close to each other

DC-Block and CM choke for ICM

changed from ICM.sch to LVS1.sch

9 | | 10

10M resistors split in two for reliability

Place close to converter input

Jumper PWR SEL deleted

+VIa 22

M1 Grounding Option 1:
Add spring clip (SC1) to PCB next to M1
1) Place SC1 footprint next to M1 outline.
2) Observe proper spacing (2.5mm-3.0mm)
3) SC1 footprint is detailed here:
https://cdn.harwin.com/pdfs/S1941R.pdf
4) See also sketch to right:
5) Footprint "SPRING CONTACT SM" added to Custom2.PCBLIB

Pad for Spring Contact SC2
(with solder paste)

Pad for Spring Contact SC1

Y:\My Hardware\Altium\IceCube\Mini-Mainboard\MMB_Controller (2-27-2020 2-48-15 PM)\Design Projects\Mini MB\LVS1.SchDoc
